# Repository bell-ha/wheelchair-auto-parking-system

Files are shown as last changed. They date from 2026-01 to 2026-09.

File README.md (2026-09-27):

<div align="center">

# 전동휠체어 자동 주차 시스템

운전하는 사용자를 위한 전동휠체어 적재






2025.12 ~ 진행 중 · 3인 팀 · 위치추정과 인식, 통합 담당 · ITRC 과제

</div>

---

## Impact

| | |
|---|---|
| **카메라를 옮긴 재설계** | 먼 구간이 안 찍혀 전면 개편 · 차량 어라운드뷰 → 휠체어 탑재 |
| **직접 구성한 데이터** | 실차 121장 · 목업 60장 직접 라벨링 · 차량 부품 6종, 번호판을 자로 활용 |
| **IMU로 회전 보정** | 앞바퀴가 캐스터라 틀어짐을 못 읽어, 각도 대신 회전속도를 맞춰 진동 제거 |
| **하드웨어 최적화** | 디코딩이 코어 하나를 91% 점유 · 갱신 주기 분리로 4 → 15 FPS 향상 |

---

## Background

전동휠체어 사용자는 차량에 탑승한 뒤, 밖에 남겨진 휠체어를 스스로 실을 수 없습니다.
이 과정에는 반드시 타인의 도움이 필요하고, 혼자 운전하는 사용자에게는 외출 자체의 제약이 됩니다.

본 연구에서는 **기아 RAY 자가운전 차량을 기준으로, 휠체어가 스스로 트렁크까지 가서
주차 및 출차하는 시스템**을 제안합니다.

설계 원칙은 처음부터 **범용성**이었습니다.

- 추가 센서 장착을 최소화한다
- 특정 차량·휠체어 모델에 종속되지 않는다
- 차량에 이미 달려 있는 것(어라운드뷰 카메라)을 최대한 활용한다

| | **V1** (중단) | **V2** (진행 중) | **V3** (검토) |
|---|---|---|---|
| 카메라 위치 | **차량** — 어라운드뷰 2대 | **휠체어** — 탑재 카메라 | 없음 |
| 무엇을 보나 | 휠체어의 ArUco 마커 | 차량 부위 6종 (딥러닝) | 전파 (UWB) |
| 위치 추정 | 탑뷰 맵 좌표 | 번호판 실측 규격 기반 단안 | 거리 측정 ±10 cm |
| 제어 | A\* 경로계획 → CAN | IBVS + 초음파 + IMU → 조이스틱 | |
| **막힌 곳** | **먼 구간이 안 보인다** | **하드웨어가 불어났다** | |

---

## Architecture

### V1 — 차가 휠체어를 본다

<div align="center">

</div>

### V2 — 휠체어가 차를 본다

<div align="center">

</div>

---

## Contributions

근거와 수식, 측정 전문은 [설계 노트](docs/DESIGN.md)에 있습니다.

### V1 — 차량 카메라로 위치 추정

차량에 장착되어 있는 어라운드뷰 카메라로 휠체어의 ArUco 마커를 보고 위치를 추정합니다.
휠체어에 아무것도 달지 않아도 되는, 범용성 원칙에 가장 충실한 선택이었습니다.

- 어안 왜곡을 편 뒤 SolvePnP로 마커까지의 위치와 회전을 구함
- 오차가 거리와 각도에 따라 일정한 방향으로 치우쳐, 그 편향을 학습으로 상쇄하는 보정층을 설계
- 칼만 필터로 시계열을 안정화

**8단계 파이프라인 중 7단계가 실기체에서 동작했습니다.**
캘리브레이션 → 탑뷰 합성 → 위치추정 → A\* 경로계획 → CAN 제어까지 이어졌습니다.

<div align="center">
<a href="https://youtu.be/o30saxUv7JM">

</a>
<br><sub>어안 2뷰(좌·후방)로 마커를 추적하고 탑뷰 맵에 위치를 찍는다 · <a href="https://youtu.be/o30saxUv7JM">youtu.be/o30saxUv7JM</a></sub>
</div>

### V2 — 휠체어 카메라로 위치 추정

휠체어에 실은 카메라로 차량의 특징을 봅니다.
공개 데이터셋이 실차에서 듣지 않아 직접 촬영하고 라벨링해 학습시켰습니다.

- 번호판, 엠블럼, 손잡이, 주유구, 후미등, 사이드미러 **부위 6종을 개별 탐지**
- **번호판을 기준 자로** 삼아 거리를 추정 — 335 × 155 mm가 국가 표준으로 고정되어 있음
- 목업을 학습시킨 뒤 **검출이 6배 증가**

<div align="center">
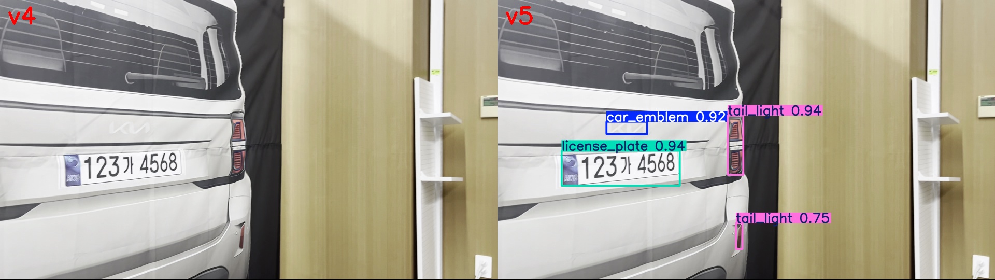
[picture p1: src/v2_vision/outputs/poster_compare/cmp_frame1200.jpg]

<br><sub>도메인 데이터 추가 학습 전(좌)과 후(우). 같은 프레임에서 검출 0건 → 4건</sub>
</div>

### 두 가지 센서로 정렬

사이드미러로 시야를 맞춘 뒤, 초음파로 평행을 맞춥니다.
한 센서로 끝까지 가지 않고 **구간마다 기준을 넘깁니다.**

- **VISION** — 사이드미러의 화면 위치와 크기를 목표 자세에 맞춤
- **SONAR** — 측면 초음파 앞뒤 거리 차이로 차량과 평행하게
- 두 국면 모두 **여덟 프레임 연속** 허용범위여야 다음으로 넘어감

<div align="center">

</div>

### 하드웨어 최적화

휠체어에 장착할 컴퓨터라는 제약에서 출발해 **Jetson Nano 4GB**에 얹었습니다.
4 FPS에 머물던 것을 지속 15 FPS, 프레임당 추론 42 ms로 끌어올렸습니다.

- 카메라를 30 fps로 받으면 디코딩 스레드가 **코어 하나를 91% 점유**해 추론이 쓸 CPU를 뺏음
- 카메라를 15 fps로 낮추고 화면 갱신을 10 Hz로 분리
- 모델 로드 중 프리징은 스왑 부족이어서 4 GB로 확장

| 처리 속도 | 프레임당 추론 | RAM | GPU | 전력 | 온도 |
|---|---|---|---|---|---|
| **지속 15 FPS** (최대 22) | 42 ms | 3.55 / 3.96 GB | 평균 35% | 5.8 W | 47~49 ℃ (팬 없음) |

---

## Troubleshooting

### 튜닝으로 풀 문제와 설계를 바꿔야 하는 문제

- **문제** 먼 구간의 오차가 줄지 않음. 보정을 더해도 그대로
- **원인** 거리가 멀어 그 구간이 아예 찍히지 않음. 파라미터로 풀 문제가 아니었음
- **해결** 마커를 키울 수도, 보정으로 메울 수도 없음. 그 근거로, 카메라를 휠체어로 옮기자고 제안
- **결과** V1에서 V2로 설계를 바꿈. 경로 생성은 그대로 쓸 수 있음. 팀원 작업은 영향 없음

> **캘리브레이션은 왜곡을 펴는 것이지, 찍히지 않은 곳을 보이게 하지 못합니다.**

<div align="center">

<br><sub>카메라를 고정된 쪽(차량)에 두느냐, 움직이는 쪽(휠체어)에 두느냐</sub>
</div>

### 직진 중 좌우로 진동

- **문제** 직진 명령을 줘도 똑바로 못 감. 좌우로 흔들림
- **원인** 앞바퀴가 캐스터라 이전 방향으로 휨. 그 틀어짐을 읽을 센서가 없음. IMU로 각도를 재 P제어로 되돌림. 방위오차가 1.2°인데 자이로는 −17.7°/s. 도착 순간 브레이크가 없어 반대로 넘어감
- **해결** 각도로 목표 회전속도를 정함. 자이로가 그 속도를 맞추는 구조로 교체. 적분항이 캐스터의 틀어짐을 주행 중 학습
- **결과** 가까울수록 스스로 감속. 50° 벗어난 상태에서 약 7초에 복귀

### Jetson Nano에서 프리징

- **문제** 추론을 돌리면 보드가 멈춤. 아무 응답이 없음
- **원인** 메모리가 모자라 스왑이 부족해짐
- **해결** 스왑을 4GB로 늘림. 입력 해상도를 320픽셀로 낮춤
- **결과** 15 FPS로 지속 구동. 추론에 42 ms

---

## 실행

Python 3.10 (`ultralytics`, `opencv-python`)

```bash
cd src/v2_vision

# 부위 탐지
python3.10 scripts/test_video.py raw_videos/레이영상_1.mov models/best_v5_poster.pt

# 거리·자세 HUD
python3.10 scripts/distance_video.py raw_videos/레이영상_1.mov models/best_v4_6cls.pt

# Jetson 실시간
cd jetson_nano && python3 main.py
```

결과 영상·데이터셋 원본 18개(약 3.8 GB)는 용량 제한으로 제외했습니다 (`.gitignore` 참고).

---

## 한계

### 자동으로 도는 구간 (1·2단계)

`AlignmentPlanner`가 VISION → SONAR 두 국면을 돌린다. 여기서 관측된 문제다.

| | 남은 문제 |
|---|---|
| 1. IBVS 초기 정렬 | 좌우로 진동하며 특징을 매칭하지 못하는 구간이 있다. YOLO를 올리며 메모리가 1 GB 늘어 **3.6 / 4 GB**까지 찼다 |
| 2. 초음파 평행 | 횡방향 간격은 잡히지만 **x축 정렬은 IBVS 오차가 크다** |

### 수동으로 이은 구간 (3~8단계)

**단계를 잇는 시퀀서를 붙이지 못했다.** 아래는 설계한 순서에서 예상되거나
수동 조작 중 관측한 것이지, 자동 주행에서 측정한 값이 아니다.

| 단계 | 남은 문제 |
|---|---|
| 3 · 5 · 8. 직·후진 | 캐스터 휠 정렬에 따라 이동 방향이 휜다. 직진 방위 유지만 IMU로 잡았다 |
| 4. 70° 회전 | **고정값이라** 시작 위치가 달라지면 따라가지 못한다 |
| 6. IBVS 후방 정렬 | 좌측 초음파 2개 간격이 짧고 완전한 후방이 아니라 매번 같은 위치로 수렴하지 않는다 |
| 7. IMU 정면 회전 | 전방 초음파가 하나뿐이라 평행 여부를 알 수 없어 IMU 오차가 그대로 남는다 |

### 장비와 기록

| | |
|---|---|
| **측면 초음파 4개가 전부 `-1`** | 전방은 정상. 2단계 SONAR 정렬이 지금 상태로는 돌지 않는다 |
| 텔레메트리 3 Hz | 초음파를 순서대로 재느라 느리다. IMU만 20 Hz로 따로 쏘면 보정 품질이 오른다 |
| `ultrasound/sample.ino` 불일치 | 실제 플래시된 펌웨어에 있는 MPU6050 코드가 저장소 버전에 없다 |

### V3 — 보지 않는 쪽으로

1·2·6은 시야에 의존하는 정렬이고, 3·5·8은 관측 불가능한 바퀴 상태에서 비롯된다.
개별 단계를 튜닝하는 대신 **시야에 의존하지 않는 측위**로 바꾸면 상당수가 함께 사라진다.
**UWB**를 검토 중이다 — 오차 ±10 cm, 현대·기아가 디지털키에 이미 상용화, 설치 위치·각도 제약이 적다.

> **조사와 장비 구매까지 진행했다. 실험은 시작하지 않았다.**

---

## 문서

| | |
|---|---|
| [설계 노트 (DESIGN)](docs/DESIGN.md) | V1 보정층 수식 · V2 학습 이력 · 9단계 설계 · V3 검토 |
| [V2 모델 학습 이력](src/v2_vision/README.md) | v1 → v5 학습 기록 |
| [거리추정 정리](src/v2_vision/거리추정_정리.md) | 핀홀 · yaw · bearing 유도 |
| [Jetson 부하 테스트](src/v2_vision/jetson_부하테스트_보고서.md) | 전체 측정 기록 |
| [세그멘테이션 실험](src/v2_vision/seg_experiment/RESULTS.md) | 대안 검토 |
| [V1 전체 정리](src/v1_aroundview/NOTES.md) | 8단계 파이프라인 |
| [발표자료](files/) | 0301 · 0821 · 0901 |
| [프로젝트 소개 페이지](https://bell-ha.github.io/projects/wheelchair-parking/) | 요약 · 도면 · 데모 |

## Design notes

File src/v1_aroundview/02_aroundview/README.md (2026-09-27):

# 02_aroundview — 탑뷰 합성

여기의 캘리브레이션은 어라운드뷰 전용이다. `01_calibration/` 의 것과 별개다.

| 파일 | 하는 일 |
|---|---|
| `calibration_left.py` · `calibration_rear.py` | 일반 카메라 캘리브레이션 |
| `aroundview_left.py` · `aroundview_rear.py` | 캘리브레이션 결과에 점을 찍어 어라운드뷰 생성 |
| `pickpoint.py` | `point_*.py` 가 쓸 점만 골라 저장 |
| `point_left.py` · `point_rear.py` | 저장한 점으로 어라운드뷰 생성 |
| `main.py` | Left·Rear 를 합쳐 하나의 캔버스로 |

`Data/` — 캘리브레이션 `.npz` 와 중간에 캡처한 데이터.

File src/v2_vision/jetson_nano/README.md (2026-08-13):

# jetson_nano — 젯슨 나노 배포용 폴더

카메라 실시간 추론 + 하드웨어(초음파/서보) 통합 코드 모음.
학습 코드·데이터셋은 없음 (추론 전용).

```
jetson_nano/
├── main.py                        # 통합 실행: 카메라(YOLO) + 초음파/서보(ESP32) 한 프로세스
├── hardware/                      # 🔧 공용 하드웨어 계층 — main.py와 guidance/가 같이 씀
│   ├── camera.py                  #   GStreamer 파이프라인 + Webcam (16:9/15fps 규칙 문서화)
│   └── esp32.py                   #   시리얼 프로토콜 한 벌 (텔레메트리 수신 + 서보 송신)
├── camera/
│   └── best_v5_poster.pt          # 최신 모델
├── ultrasound/
│   └── sample.ino                 # ESP32 펌웨어: 초음파 5개 + 서보 2축, JSON 프로토콜
├── guidance/
│   ├── teach.py                   # 목표 상태 저장 툴 (카메라+초음파 보면서 지도 클릭, s로 저장)
│   ├── guide.py                   # 판단: 정렬 지시 표시, --drive면 서보(조이스틱) 자동 구동
│   └── common.py                  # guidance 공용 (앵커 추출/좌표 추정/goal 저장·로드)
├── unused/                        # 대체된 코드 보관 (이유는 unused/README.md 참고)
├── requirements.txt
└── README.md
```

**구조 (3층):** 카메라/ESP32 접근 코드는 `hardware/` 공용 계층 한 벌뿐이고,
그 위에 사람조종용(`main.py`)과 판단용(`guidance/`)이 올라감 — 카메라 설정이나
시리얼 프로토콜이 바뀌면 `hardware/`(+펌웨어) 한 곳만 고치면 전체 반영됨.

## 젯슨 접속 (SSH)

맥과 젯슨이 같은 네트워크(같은 공유기)에 있어야 함. 계정 `jetson`, 호스트명 `nano`.

```bash
# 맥에서 — 호스트명으로 접속 (mDNS)
ssh jetson@nano.local

# 안 되면 IP로 (192.168.0.254)
ssh jetson@<JETSON_IP>
```

- IP 확인: 젯슨에서 `hostname -I`, 또는 공유기 관리 페이지 접속기기 목록.
- IP가 자꾸 바뀌면 공유기에서 DHCP 고정(예약) 해두기.
- 비밀번호 생략하려면 맥에서 한 번만: `ssh-copy-id jetson@nano.local`

## GitHub에서 받기

리포 전체는 수 GB라 이 폴더만 sparse checkout으로 받는다.

```bash
cd ~/GitHub
git clone --depth 1 --filter=blob:none --no-checkout \
    https://github.com/bell-ha/wheelchair-auto-parking-system.git
cd wheelchair-auto-parking-system
git sparse-checkout init --cone
git sparse-checkout set src/v2_vision/jetson_nano
git checkout main
cd src/v2_vision/jetson_nano
```

## Pull / Push

```bash
# 받기 (맥 등 다른 곳에서 push된 내용)
cd ~/GitHub/wheelchair-auto-parking-system
git pull

# 젯슨에서 수정한 거 올리기 (인증은 이미 설정돼있음)
git add -A
git commit -m "젯슨: 테스트 중 수정"
git push
```

작업 시작 전 `git pull`, 끝나면 바로 `push`. 같은 파일을 양쪽에서 동시에 고치면 충돌 남.

## 설치

```bash
pip3 install -r requirements.txt

# 주의: ultralytics가 opencv-python을 의존성으로 깔기 때문에 위 명령 직후
# GStreamer 미지원 pip opencv가 다시 설치돼있음. 반드시 지워서 JetPack
# 기본 OpenCV(dist-packages, GStreamer 지원)가 쓰이게 할 것 —
# 안 지우면 USB 웹캠(C920)에서 카메라 열기가 무한 대기함.
pip3 uninstall -y opencv-python
```

`ultrasound/sample.ino`는 아두이노 IDE로 ESP32 보드에 업로드 (젯슨 아님).
Jetson과 ESP32는 USB 케이블로 직결, 포트는 `/dev/ttyUSB0`, 115200bps.

## 실행 (통합 조종석 — main.py)

```bash
cd ~/GitHub/wheelchair-auto-parking-system/src/v2_vision/jetson_nano
python3 main.py        # 모델 경로 생략 시 camera/best_v5_poster.pt 사용
```

**키: A/D/W/S = 서보 수동 조작 | G = 자동모드 토글 | Q = 종료**

- **수동 모드(기본)**: A/D/W/S로 서보(조이스틱) 직접 조작
- **자동 모드(G)**: guidance 판단기가 teach로 저장한 goal을 향해 서보를 스스로
  조작. **자동 중 아무 이동키나 누르면 즉시 수동 복귀 + 정지** (비상 개입).
  goal 파일이 없으면 자동모드는 비활성 (화면에 사유 표시)
- **터미널(curses)**: 검출/FPS, 자동모드 지시·판단근거(du/scale/sonarErr)·전송각,
  초음파 5개, 서보 에코, 수신시간을 실시간 표시
- **HDMI 카메라 창**: 검출 박스 + 목표 ✕마커 + 현재 앵커 ○ + 자동모드 지시 배너 +
  오른쪽에 미니맵(CAR·목표·현재위치 추정). 기본 절반 크기(`--display-scale 0.5`),
  `--no-show`로 끄기 가능
- ESP32가 안 붙어있으면 `--no-servo`로 카메라만 테스트. 그 외 `--help`
- 자동모드 서보 방향이 반대면 `--invert-x`/`--invert-y`, 편향각은
  `--turn-deg`/`--drive-deg` (기본 ±10°)

시작 직후 "모델 워밍업 중..."이 30초~1분 정도 뜨는 건 정상 (젯슨 첫 추론 특성).
워밍업이 끝나야 터미널 화면으로 전환됨.

`--cam-width`/`--cam-height`는 16:9 조합(1280x720, 1920x1080 등)으로 맞출 것 — C920은
4:3 해상도(640x480, 800x600, 1280x960)를 요청하면 카메라 자체가 좌우를 크롭해서
화각이 좁아짐. 1920x1080은 화면은 더 선명하지만 이 보드(RAM 4GB) 기준 메모리 여유가
빠듯해서(스왑 발생 확인됨) 1280x720 권장.

부품 단독 점검: 카메라만 → `main.py --no-servo`, ESP32만(카메라 없이) →
`unused/test_sample.py` 꺼내 쓰기 (자세한 건 unused/README.md).
부하 확인은 다른 터미널에서 `sudo tegrastats` 병행 권장 (GPU 사용률·온도·스로틀링).
자세한 결과는 [../jetson_부하테스트_보고서.md](../jetson_부하테스트_보고서.md) 참고.

## 자동 정렬 (guidance/)

teach & repeat 방식: `teach.py`로 목표 상태(사이드미러 위치·크기 + 측면 초음파 쌍 +
지도에 클릭한 목표 좌표)를 JSON으로 저장해두면, 판단기(`common.AlignmentPlanner`)가
현재 상태와 비교해 "TURN LEFT / MOVE FORWARD / ALIGNED - STOP" 지시를 만듦.
①VISION 단계(사이드미러 정렬) → ②SONAR 단계(측면 초음파 앞/뒤 차이로 평행 정렬) 순서.

**판단기는 main.py 자동모드(G키)와 guide.py가 공유** — 평소엔 main.py G키가
주 사용 경로고, guide.py는 guidance만 따로 돌리고 싶을 때의 단독 진입점.

```bash
python3 guidance/teach.py            # (선행 필수) 목표 저장: 지도 클릭 + s, q 종료
python3 guidance/guide.py            # 단독 실행: 지시 화면 표시만 (기본, 안전)
python3 guidance/guide.py --drive    # 단독 실행 + 서보(조이스틱) 실제 구동
```

`--drive` 모드: TURN/MOVE 지시가 서보 X/Y 편향(기본 ±10°, `--turn-deg`/`--drive-deg`)으로
전송되고, STOP류 지시·타겟 상실·종료 시엔 무조건 중앙(90/90=정지)으로 복귀함.
**첫 구동 테스트는 반드시 휠체어 전원을 끄거나 바퀴를 띄운 상태에서** 서보가
의도한 방향으로 움직이는지 확인하고, 반대로 움직이면 `--invert-x`/`--invert-y`로 보정.

- 카메라·시리얼을 main.py와 공유하므로 **동시 실행 불가**
- 초음파 기준 거리(SONAR_BASELINE=0.315m)는 `sample.ino`의 `SIDE_SENSOR_SPACING_CM=31.5`와
  맞춰둔 값 — 센서 간격을 바꾸면 양쪽 다 수정할 것

## 젯슨나노 종료
```bash
sudo shutdown -h now
```

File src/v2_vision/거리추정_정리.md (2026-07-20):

# 거리·각도 추정 작업 정리 (2026-07-09~10)

휠체어프로젝트의 다음 단계 작업 기록. README.md(프로젝트 전반)와 함께 읽을 것.

## 무엇을 만들었나

`scripts/distance_video.py` (신규) — v4 탐지 모델 위에 **번호판 실측 규격 기반
단안 거리·각도·방위각 추정**을 얹은 스크립트. 기존 test_video.py는 안 건드림.

실행:
```
python3.10 scripts/distance_video.py raw_videos/레이영상_1.mov models/best_v4_6cls.pt --conf 0.15
```
결과는 `outputs/distance/<영상>_dist.mp4` (좌상단 HUD로 값 표시).
※ 환경 주의: ultralytics/opencv는 **python3.10**(Frameworks)에 설치돼 있음.
README에는 3.11로 적혀 있는데 실제로는 3.10 (README 미수정).

## HUD에 표시되는 3가지 값 (도킹 제어의 3요소)

| 값 | 계산 방법 | 의미 (휠체어 관점) |
|---|---|---|
| 거리 (m) | 번호판 높이 155mm × 핀홀 공식: D = H_real·f / h_px | 얼마나 남았나 |
| yaw (deg, ±) | 크기 = 폭/높이 비율 acos, 부호 = 꼭짓점 키스톤(좌/우 변 길이 비교). 음수 = 왼쪽(L)에서 봄 | 차가 얼마나 비스듬한가 → 접근 자세 |
| bearing (deg, ±) | atan((번호판 중심 x − 화면중심) / f). 왼쪽 음수 | 차가 내 시야 어느 쪽인가 → 조향 |

- 레이 후면 번호판 실측 규격: **단형 335×155mm** (영상에서 육안 확인, "66라 5623")
- 초점거리: iPhone 13 mini 1x(35mm환산 26mm) 가정 → 1920px 기준 f≈1387px.
  **미보정 상태라 거리에 ±10~15% 스케일 오차 가능.** 줄자로 잰 거리에서 찍은
  영상으로 `--calib 1.0` 실행하면 `scripts/camera_calib.json`에 저장돼 자동 보정됨 (아직 안 함)
- 모든 값은 EMA(α=0.3)로 프레임 간 스무딩

## 핵심 구현 디테일 (수정 시 알아야 할 것)

1. **화면 경계에 잘린 번호판은 무시** — 잘린 박스는 작게 잡혀 거리가 부풀려짐
2. **yaw 부호(키스톤)**: YOLO 박스 크롭 → Otsu 이진화 → `RETR_LIST`(내부 윤곽 포함;
   흰 차체가 번호판을 둘러싸면 번호판 면이 blob 속 구멍이 되기 때문) → 4각형 후보 중
   크롭 경계에 안 닿는 것 우선 → 크기(YOLO 박스의 0.5~1.2배)·비율(0.6~4.5) 검증.
   좌/우 변 길이는 유클리드 거리(카메라 roll에 안전). 검출 실패 시 부호 없이 "(?)"
3. **키스톤으로 각도 "크기"까지 재는 건 포기** — 꼭짓점 1~2px 오차에 수십 도가
   흔들림(실측 -46° 오류 경험). 크기는 비율(acos) 방식이 안정적
4. `iou=0.5`로 predict — 같은 부위 중복 박스 억제
5. "가장 큰 번호판 박스"를 추적하므로 **다른 차 번호판을 따라갈 수 있음** (목표 차량
   필터 미구현 — 알려진 한계)

## 후미등 간격 방식 (실험, `--tail` 플래그, 기본 꺼짐)

아이디어: 번호판이 좌우 후미등의 정중앙(간격 실측 추정 1.3m) → 좌우 간격 비대칭으로
부호 있는 yaw. 기준선이 길어 원거리에서 유리할 것으로 기대했으나 실영상 검증 결과:
- 근거리(<3m): 후미등이 모서리를 감싸는 입체 렌즈라 박스 중심이 밀려 각도 과장
- 원거리(>7m): 신호가 거리²에 반비례해 박스 떨림에 묻힘 (±90° 포화)
- 다중 차량: 다른 차 후미등과 짝지어짐
방어 장치(위/아래 쌍 매칭 + 두 쌍 일치 검증 + 물리 크기 검증 + 3~7m 게이트)를 넣어
자기모순은 없어졌지만, **현재 영상 3개에는 레이가 3~7m 후면에 나오는 구간이 없어서
레이 대상 검증 미완**. 살리려면 7~8m 후면 직진 접근 영상 필요.

## 검증된 결과 (실영상 육안 확인)

- 정면 1.2m 후면: 거리 1.20m, yaw ~0(front) ✓
- 후면 오른쪽 45° (영상1 1초): 1.48m, **yaw +49°(R)**, bearing -21° ✓ (부호 모두 정확)
- 좁은 통로 오른쪽 비스듬 (영상3 20초): 0.83m, **+66°(R)** ✓
- 왼쪽 치우친 후면 (영상1 10초): -25°(L) ✓
- 거리 중앙값: 영상1 1.48m / 영상2 4.11m / 영상3 0.87m (장면과 부합)

## 센서/하드웨어 계획 (사용자 구상)

- **카메라를 팬 모터에 장착 예정** → 모터가 번호판을 화면 중앙에 추적.
  이때 화면상 bearing은 모터 제어 오차 신호가 되고, **모터 인코더 각도가 곧
  "휠체어 몸통 기준 차의 방향"**(= 조향 신호). yaw는 카메라를 돌려도 안 변함
  (위치 관계로 정해지는 값). 통합 시 `총 bearing = 모터각 + 화면 bearing`
- **초음파 센서**: 최근접(<1m) depth + 충돌 방지 담당. 비전은 식별·정렬 담당

## 다음 할 일

1. 촬영 1세션으로 3가지 해결: (a) 캘리브레이션용 줄자 1.0m 컷,
   (b) 후미등 방식 검증용 7~8m 후면 직진 접근, (c) 실배치 특화용 다각도 촬영
2. **v5 학습 계획**: `sliding_door`(+ 필요시 `door_open`) 클래스 추가 — 레이는
   조수석 쪽이 B필러 없는 슬라이딩 도어(휠체어 승하차 방향). 공공 데이터에 없으니
   후미등 때처럼 레이 데이터 + 오버샘플링. 미러 데이터도 보강(오탐 확인됨, mAP .754)
3. 문손잡이: 거리 측정용으론 부적합(3D 곡면, 박스 비율 0.14~5.6 요동 실측).
   **조향 목표(bearing) + 차 기하 결합**으로 사용. 앞문/슬라이딩문 손잡이 구분 필요
4. 목표 차량 필터(다른 차 번호판 배제 — 엠블럼·후미등 동반 검출 활용)
5. `git init` (잘 짜인 .gitignore가 이미 있는데 저장소가 아님)
6. README 환경 표기 수정 (python3.11 → 3.10)

## 파일 목록

- `scripts/distance_video.py` — 본 작업의 산출물 (docstring에 사용법·원리 상세)
- `outputs/distance/*_dist.mp4` — 기본 결과 3개 (영상1만 bearing 포함 최신,
  영상2·3은 bearing 추가 이전 버전)
- `outputs/distance/*_dist_tail.mp4` — `--tail` 실험본.
  ※ 영상2 tail본은 tail 미발동으로 기본본과 완전 동일(340MB 중복, 삭제 가능)
- `scripts/camera_calib.json` — 아직 없음 (캘리브레이션 후 생성됨)

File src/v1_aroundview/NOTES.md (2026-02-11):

# 프로젝트 요약 정리 (Localization / Around-View 기반 휠체어 트래킹)

## 0) 목적 및 개요

* 차량 어라운드뷰(서라운드뷰) 카메라 2대(Left, Rear)로 휠체어에 부착된 ArUco 마커를 감지하여 휠체어의 위치를 추정한다.
* 제어 신호는 4가지:

  * **F**(전진), **B**(후진), **R**(오른쪽 회전), **L**(왼쪽 회전)

---

## 1) 카메라 캘리브레이션 데이터 (Localization 용)

### 1-1. 공통 데이터

두 카메라가 동일 렌즈 모델이라 파라미터를 공유한다.

* **Camera Matrix (`K`)**

  * `[[601.719, 0, 630.477], [0, 601.345, 367.212], [0, 0, 1]]`
  * 의미: 초점거리 및 주점(중심점)

* **Distortion (`D`)**
  * `[-0.18496, 0.02541, -0.01068, 0.00322]`
  * 의미: Fisheye 왜곡 계수
  
* **Marker Size (`size`)**
  * 0.25 m (25 cm) : ArUco 마커 실제 크기

* **RMS Error (`rms`)**
  * **0.5898**
  * 메모: “시스템 신뢰도(양호)”로 판단

### 1-2. 카메라별 설치/제어 보정값 (Extrinsic & Control)
설치 위치가 다르므로 각도 계산/제어용 보정값을 카메라별로 적용한다.

| 항목            | Rear(후방) | Left(측방) | 설명                          |
| ------------- | -------: | -------: | --------------------------- |
| 각도 감도 `SENS`  |      1.6 |      1.6 | 어안 외곽 압축 상쇄 + 실제 각도 동기화     |
| 설치 보정각 `INST` |      0.0 |    113.0 | Left: 서쪽 90° + 남쪽 23° 편향 상쇄 |
| 영점 오프셋 `OFFS` |      0.0 |    50.84 | 휠체어 정북향 시 최종 Yaw를 0으로 고정    |

---

## 2) 차량/레이(차체) 기본 치수 가정

* **폭(차량 + 사이드미러 포함)**

  * 1595mm + 사이드미러 각 178mm = **1951mm ≈ 약 2m로 가정**

* **길이(전장)**
  * 3595mm = **약 3.6m로 가정**

참고 링크(자료 출처로 사용 예정):

* [https://carmia.co.kr/html/s0603.php?d=v&tbl=b0603&seq=833&page=1&s_sel=&s_key=&s_cat=](https://carmia.co.kr/html/s0603.php?d=v&tbl=b0603&seq=833&page=1&s_sel=&s_key=&s_cat=)
* [https://m.oh-car.co.kr/goods/goods_view.php?goodsNo=1000593989](https://m.oh-car.co.kr/goods/goods_view.php?goodsNo=1000593989)

---

## 3) 어라운드뷰 카메라 설치 위치/각도 (추정 포함)

### 3-1. Left 카메라 (사이드미러 아래)

* **설치 위치**: 차량 왼쪽, 사이드미러 아래
* **설치 높이**: 1100mm

* **Pitch(아래 바라보는 각도)**
  * 실제 설정: **40도**(아래에서 20도라고 했으나, 40도까지밖에 안됨)

* **Yaw(좌우 방향)**
  * 정확한 수치는 없음
  * “앞 뒤 다 나오게” 조정
  * 추가로: 왼쪽 자체를 바라보는 방향에서 더 뒤로 23도 틀어져 있음 -> 157도

### 3-2. Rear 카메라 (번호등 아래)

* **설치 위치**: 차량 후면 중앙 번호등 아래
* **설치 높이**: 1055mm

* **Pitch(아래 바라보는 각도)**
  * SVM 매뉴얼 기준: 아래로 5~60도(범위 언급)
  * 실제 사용: 
  50도

---
## 4) 휠체어(실제) 정보 + 마커 정보

### 4-1. “실제 휠체어(기본)” 치수 및 마커(초기 설명)
* **휠체어 폭/길이**
    * 폭 57cm, 길이 100cm

* **앞 ID:0**
  * 마커 높이:70c
  * 13도 위를 향함

* **뒤 ID:1**
  * 마커 높이: **56cm**
---

## 5) “휠체어 없이 트래서(Tracker) 운용” 시나리오(별도 세팅)
* 앞 ID:0 마커 높이: 70cm
* 뒤 ID:1 마커 높이: 70cm
* 대상 폭/길이
  * 폭 55cm, 길이 66cm

---

## 6) 지도/프레임 좌표계 및 금지구역(차량 영역)

* 전체 프레임: **1500 x 1500**
* 어라운드뷰 프레임: **600 x 720**(1500x1500기준에서 중앙)
* 어라운드뷰 프레임 내 **자동차 구역(진입 불가 폴리곤/사각형)**
  * 꼭짓점: **(200,180), (400,180), (400,540), (200,540)**(어라운드뷰 프레임 기준)
  * 이 영역 안으로는 들어갈 수 없음(경로 계획/제어에서 회피해야 함)

---

## 7) 카메라 기준 좌표(설치 위치) 및 목표 위치(주차/출차)(어라운드뷰 프레임 기준)

* 카메라 위치
  * **Left 카메라 위치: (200, 270)**
  * **Rear 카메라 위치: (300, 540)**

* 주차 시(도킹/정렬) 목표 상태:
  * **(300,600)** 위치에서 **Rear를 바라보고 있는 상태**

* 출차 시 목표 상태:
  * **(150,360)** 위치에서 **Left를 바라보고 있는 상태**

---

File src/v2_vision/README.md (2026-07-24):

# 휠체어프로젝트 — 자동차 부위 탐지 (YOLOv8)

전동휠체어가 차량에 접근/인식하기 위한 자동차 부위 6종 탐지 모델.

## 전역 클래스 표준 (자연어 언더바, nc=6)
0:car_emblem  1:door_handle  2:fuel_cap  3:license_plate  4:side_mirror  5:tail_light

## 폴더 구조 (2026-07-23 정리)
- raw_datasets/ : 원본 Roboflow zip (건드리지 않음). 공공 6종 + ray_roboflow_v1.zip
- models/ : best_v1_merged / best_v2_ft / best_v3_ray / best_v4_6cls(최신)
- raw_videos/ : 원본 영상 — 레이영상 1·2·3(실차) + 포스터레이.MOV(실물크기 포스터, 포스터 라벨의 원본)
- my_data/labeled/ray_all/ : 실차 라벨 데이터 (6종, 121장) ★
- my_data/labeled/ray_poster/ : 포스터 라벨 데이터 (6종, 60장, 2026-07 추가) ★
- scripts/ : test_video.py, distance_video.py, live_camera.py, finetune_local.py,
             kaggle_finetune_v3.ipynb, kaggle_finetune_v4.ipynb (remap_ray.sh는 5클래스 시절 유물 — 사용 금지)
- outputs/ : 결과 영상 (v4 검출 3개 + distance HUD 3개만 보존. v3·tail 실험본은 삭제 — 스크립트로 재생성 가능)
- seg_experiment/ : 세그멘테이션 실험 기록 (RESULTS.md + 스크립트만 보존, 대용량 삭제)
- kaggle_upload/ : Kaggle 업로드용 공공 6종 .bin 로컬 백업 (캐글 데이터셋 유실 대비.
  raw_datasets zip과 내용 동일, 이름만 노트북 SOURCES 기준)
- my_data/labeled/ray_all.bin·ray_poster.bin : 라벨 폴더에서 재생성되는 업로드용 압축본 (git 미추적)

## 모델 버전 이력
- v1_merged : 5종 개별→통합. 번호판 배경충돌로 억제됨
- v2_ft     : 신형 번호판 fine-tune. 레이영상 plate 13→80프레임
- v3_ray    : 레이 도메인 데이터(5종) 추가 fine-tune. 번호판 실영상 개선
- v4_6cls   : 후미등(tail_light) 추가, 6클래스 새 학습 (2026.07.06)
              val mAP50: plate .995 / emblem .974 / handle .917 /
              fuel_cap .878 / tail_light .811 / mirror .754
- v5_poster : 포스터(실물크기 목업) 60장 추가, POSTER_REPEAT=12 독립 소스 (2026.07.24) ★최신
              포스터 환경 대폭 개선 (plate 검출 프레임 6배, conf 0.26→0.89)
              ※ 실차 성능 재검증 미완 — 자세한 내용은 포스터_위치추정_정리.md

## 학습 방법 (요약)
- Kaggle T4에서 학습. 노트북: scripts/kaggle_finetune_v4.ipynb
- Add Input: 공공 6종 bin + ray_all.bin (한 데이터셋에 다 넣어도 됨)
- 자세한 준비/업로드 순서: kaggle_학습방법.md 참고
- 클래스 5→6 바뀌어 v3 이어받기 불가 → yolov8n부터 새 학습
- 레이는 후미등 유일 출처라 oversampling(RAY_REPEAT)으로 비중 확보

## 다음 할 일 (2026-07-24 갱신 — 상세는 포스터_위치추정_정리.md '남은 일')
- 포스터 줄자 실측 4개 → 위치추정 랜드마크 좌표 확정
- f 캘리브레이션 (--calib), v5 실차 성능 확인 (레이영상 1~3 재실행)
- 도킹 제어 개발 (진입점 계산 → 2단계 접근 → IBVS 정밀 정렬)

## 핵심 교훈
1. 부분 라벨=배경충돌: 병합 시 라벨 안 된 대상이 배경으로 학습돼 검출이 죽음
   (번호판 v1, 후미등도 공공데이터엔 없어 레이로만 배움)
2. 리허설 fine-tune: 새 데이터+기존 클래스 일부를 섞으면 망각 없이 특정 클래스 보강
3. val≠실전: val 지표 높아도 진짜 판정은 "내 영상에서 몇 프레임 잡히나"
4. 도메인 불일치가 진짜 원인: 해결은 학습량이 아니라 내 영상 도메인 데이터
5. 클래스 추가 시 재매핑: Roboflow 알파벳순 → 전역 표준 순서로 맞춰야 함
   (auto-label은 세그멘테이션 라벨 뱉음 → 박스 변환 필요. v4 노트북이 자동 처리)

## 환경 메모
- 로컬 맥: python3(3.14)는 MPS 안 됨. python3.11 사용 (opencv 등은 3.11에 설치)
- 추론: python3.11 scripts/test_video.py <영상> <모델.pt> <conf>
- 학습은 Kaggle T4 권장 (무료, 환경문제 없음)
- Kaggle zip data.yaml 충돌 → .bin으로 확장자 바꿔 회피

## 다음 단계: 실배치 레이 특화 (계획)
- 실제 테스트/배치할 레이 1대를 확정
- 그 차를 다양한 상황(각도·거리·조명·낮밤)으로 충분히 촬영·라벨링
- 일반화보다 "그 차 확실히 잡기" 목표 → 해당 레이에 의도적으로 특화(overfit 허용)
- 주의: "한 대"여도 다양한 상황이 필요 (같은 장면만 과적합하면 실주행서 약함)
- RAY_REPEAT 높이고, 그 차 데이터 비중 크게 잡아 학습

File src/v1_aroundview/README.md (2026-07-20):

# V1 — 차량 어라운드뷰 기반 (개발 중단)

차량에 장착한 어라운드뷰 카메라 2대(Left, Rear)로 휠체어에 부착된 ArUco 마커를
검출해 휠체어 위치를 추정하고, A* 경로계획으로 제어 신호(F/B/L/R)를 만들어
휠체어를 차량 옆 주차 위치까지 유도하는 파이프라인.

> **중단 사유**: 어안(fisheye) 카메라 캘리브레이션의 누적 오차로 맵 좌표가 튀는
> 문제를 07_map_calibration에서 끝까지 잡지 못함. 카메라를 차량이 아닌
> **휠체어에 탑재**하는 방식([V2](../v2_vision/))으로 전환.

## 환경 설정

```bash
source ../venv/bin/activate   # 가상환경 (repo에는 미포함)
pip install -r requirements.txt
```

## 폴더 구성 (파이프라인 순서)

| 폴더 | 내용 |
|---|---|
| `01_calibration/` | 체커보드 촬영 → 카메라 왜곡계수 추출 |
| `02_aroundview/` | Left/Rear 영상 정합 → 어라운드뷰(탑뷰) 합성 |
| `03_localization/` | ArUco 마커 검출로 휠체어 위치/방향 추정, 맵 생성 |
| `04_planning/` | A* 기반 경로계획 |
| `05_hardware/` | 구동부: TRACER 섀시 CAN 통신 제어 절차 |
| `06_angle_tunning/` | 각도 보정(트랙바 UI로 파라미터 튜닝) |
| `07_map_calibration/` | 최종 맵 캘리브레이션 — 오차 가중 보정, outlier 제거 시도 |
| `08_parking/` | 통합 실행: 위치추정 + 경로계획 + 제어 (수동조종 포함) |
| `command/` | 03/06 계열 통합 실험 버전 |
| `utils/` | 카메라 탐색, 녹화, ArUco 검출 등 보조 도구 |

## 기술 노트

캘리브레이션 수치, 카메라 설치 위치/각도, 좌표계 정의 등 상세 기록은
[NOTES.md](NOTES.md) 참고.

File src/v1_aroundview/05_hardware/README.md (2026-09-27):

# 05_hardware — 구동부와 차량 사양

TRACER 섀시 CAN 통신 절차는 [can_bus/README.md](can_bus/README.md) 에 있다.

## 기아 레이 내비게이션 사양 (조사)

| | |
|---|---|
| 화면 | 8인치 터치스크린 |
| CPU | 차량용 프로세서 — Nvidia Tegra 또는 Telechips 계열로 **추정** |
| RAM | 2~4 GB **추정** |
| 연결 | 기아 커넥트 — 내장 eSIM, OTA 업데이트 |

> **추정 근거** — 현대차 하드웨어가 5세대에서 RAM 2~4 GB 였고 이후 4~8 GB 로 올라갔다.
> 주요 공급사 텔레칩스의 Dolphin 시리즈 가이드에도 메모리 구성이 2~4 GB 로 나온다.
> **제조사 공식 사양이 아니다.**

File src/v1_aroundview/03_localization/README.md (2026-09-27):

# 03_localization — 휠체어 검출

| 파일 | 하는 일 |
|---|---|
| `angle_focus.py` | Left·Rear 영상에서 휠체어 검출 |
| `angle_focus_live.py` | 실시간 영상에서 휠체어 검출 |
| `main.py` | Left·Rear 에서 검출하는 최종본 |

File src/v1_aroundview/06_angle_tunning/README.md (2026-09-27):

# 06_angle_tunning — 각도 보정

트랙바 UI 로 파라미터를 맞춘다.

| 파일 | 하는 일 |
|---|---|
| `main.py` | 통합 실행 · 트랙바와 시각화 UI |
| `localization.py` | ArUco 기반 휠체어 위치·방향 추정 |
| `planner.py` | A* 경로 계획 |
| `tracker.py` | 경로 추종과 재계획 관리 |
| `visualizer.py` | 맵·경로·휠체어 상태 시각화 |

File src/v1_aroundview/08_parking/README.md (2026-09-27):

# 08_parking — 통합 실행

위치추정 · 경로계획 · 제어를 한데 묶어 돌린다.

| 파일 | 하는 일 |
|---|---|
| `main.py` | 통합 실행 |
| `control.py` | `wasd` 로 수동 조종, `x` 로 정지 |
| `localization.py` | 위치 추정 |
| `phase.py` | 단계 관리 |

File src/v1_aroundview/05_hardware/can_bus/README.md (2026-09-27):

# CAN 통신 — AgileX TRACER 섀시 제어

USB-CAN 으로 TRACER 섀시에 명령을 넣는 절차. A → F 순서로 따라간다.
**리모컨 권한을 반납(E)해야 CAN 명령이 먹고, 전진은 주기 전송이어야 한다(F).**

## A. PC(리눅스) 준비 체크리스트

### A-1) USB-CAN 인식 확인

```bash
lsusb
```

*  `OpenMoko ... CAN adapter`면 보통 `gs_usb` 계열이라 SocketCAN 바로 가능.

### A-2) 필수 패키지

```bash
sudo apt update
sudo apt install -y can-utils
```

```bash
pip3 install python-can
```

### A-3) 드라이버 로드(필요시)

```bash
sudo modprobe gs_usb
```

### A-4) can 인터페이스 생겼는지 확인

```bash
ip link | grep -E "can[0-9]"
```

* `can0` 또는 `can1`이 보여야 정상

---

## B. TRACER ↔ USB-CAN 배선 표준

1. 로봇 전원 **OFF 권장** 상태에서 배선

* **CAN_H ↔ CAN_H**
* **CAN_L ↔ CAN_L**

2. 로봇 전원 ON
* **E-stop 해제**
* 주변 안전 확보

---

## C. CAN 통신 “켜기” (비트레이트 포함)

TRACER는 **500kbps**.

```bash
sudo ip link set can0 up type can bitrate 500000
```

(인터페이스가 can1이면 can1로)

---

## D. “로봇이 말하는지(피드백)” 먼저 확인

이게 되면 배선/비트레이트/물리계층은 통과야.

```bash
candump can0
```

너처럼 `0x211`, `0x221`, `0x231` 등이 주기적으로 보이면 정상.

---

## E. 핵심: 리모컨 권한 반납(= CAN 제어 모드로 전환)

### E-1) 현재 모드 확인 (0x211)

```bash
candump can0,211:7FF
```

출력 예시:

* `00 00 ...` → **RC 모드**
* `00 01 ...` → **CAN 모드**
* `00 02 ...` → **Serial 모드**

### E-2) CAN 모드로 전환 명령 (ID 0x421)

RC를 꺼둬도 내부 모드가 RC로 남아있을 수 있어서, 이걸로 CAN 통신 전환

```bash
cansend can0 421#01
```

다시 확인:

```bash
candump can0,211:7FF
```

`00 01 ...`로 바뀌면 **모드 전환 성공**.

> 이 단계가 바로 네가 말한 “리모컨 권한 반납”에 해당.

---

## F. 전진 테스트(주기 전송이 필수)

TRACER는 보호 때문에 **500ms 이상 명령이 끊기면 0속도**로 떨어져.
그래서 “한 번 보내기”가 아니라 **20ms 주기 전송**이 필요.

아주 느리게 전진(100mm/s):

```bash
while true; do cansend can0 111#0064000000000000; usleep 20000; done
```

멈춤: `Ctrl+C`

속도 피드백 확인(선택):

```bash
candump can0,221:7FF
```

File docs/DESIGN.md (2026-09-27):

# 설계 노트

V1 에서 V2 로 넘어오며 무엇을 보고 왜 그렇게 정했는지를 남긴 글이다.
무엇을 만들었는지는 [README](../README.md) 에 있다.

수식·측정값·파일 줄 번호는 전부 당시 코드와 실험 기록에서 직접 확인한 것이다.

---

## 3. V1 — 차가 휠체어를 본다

차량에 이미 달린 어라운드뷰를 쓰면 **휠체어에 아무것도 달지 않아도 된다.** 원칙에 가장 충실한 선택이었다.

어안 카메라 2대를 캘리브레이션해 탑뷰를 합성하고, 휠체어에 붙인 25×25 cm ArUco 마커로 위치를 추정했다.

| 좌측 카메라 | 후방 카메라 | 합성 결과 |
|---|---|---|
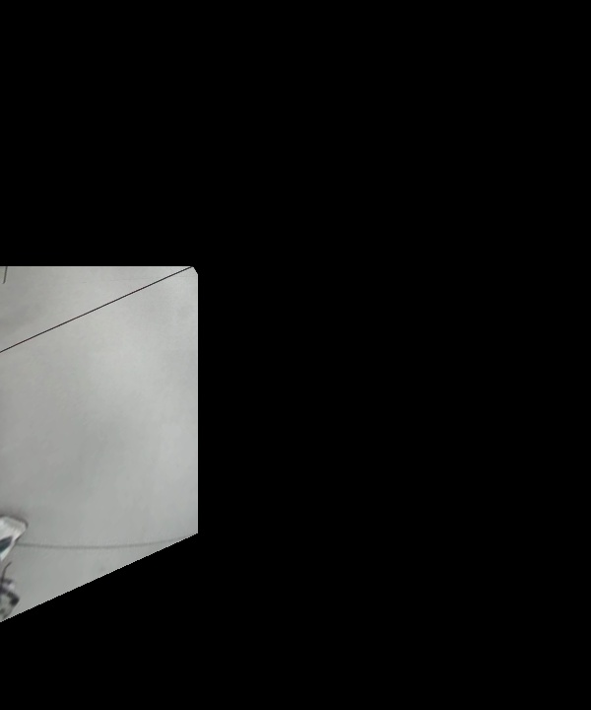
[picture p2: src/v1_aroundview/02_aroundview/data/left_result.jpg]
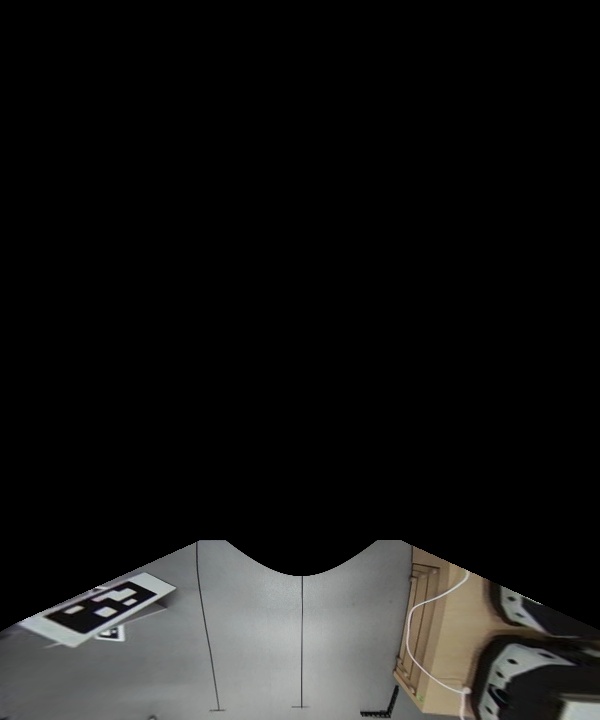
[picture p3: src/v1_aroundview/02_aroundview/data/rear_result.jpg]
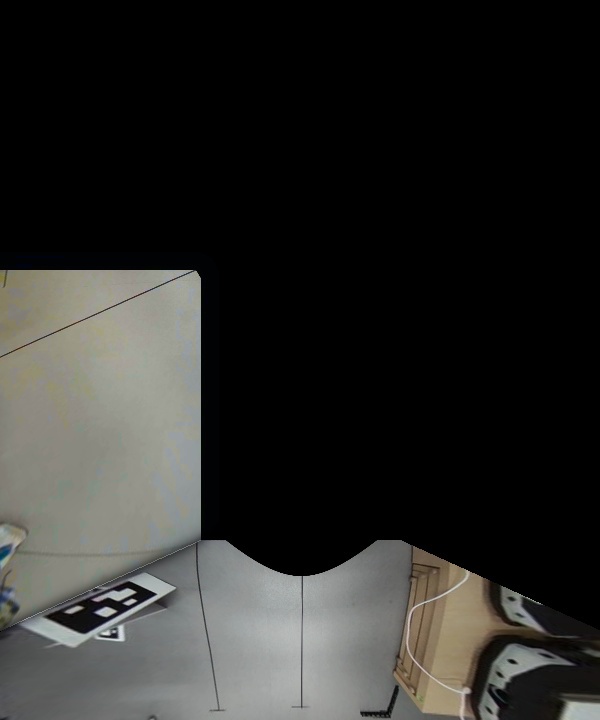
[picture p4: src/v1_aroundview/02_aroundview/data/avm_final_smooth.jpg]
|  |  |  |

### 잔차가 무작위가 아니었다

SolvePnP 결과를 그대로 쓰지 않았다. **출력 잔차가 거리·각도에 따라 체계적으로 편향된다**는 것을 확인하고 보정층을 학습으로 설계했다.

```
X = [1, g, g², b, b², v, g·b, reproj]     g 바닥거리(m) · b 화면 내 마커 각도(deg)
w* = argmin ‖Xw − y‖² + λ‖w‖²             v 마커가 카메라를 보는 각도 · reproj 재투영 오차(px)
```

여기에 전·후진 200 mm/s · 회전 0.3 rad/s 운동 모델의 칼만 필터를 얹어 시계열을 안정화했다.

| 맵 보정 전 | 보정 후 |
|---|---|
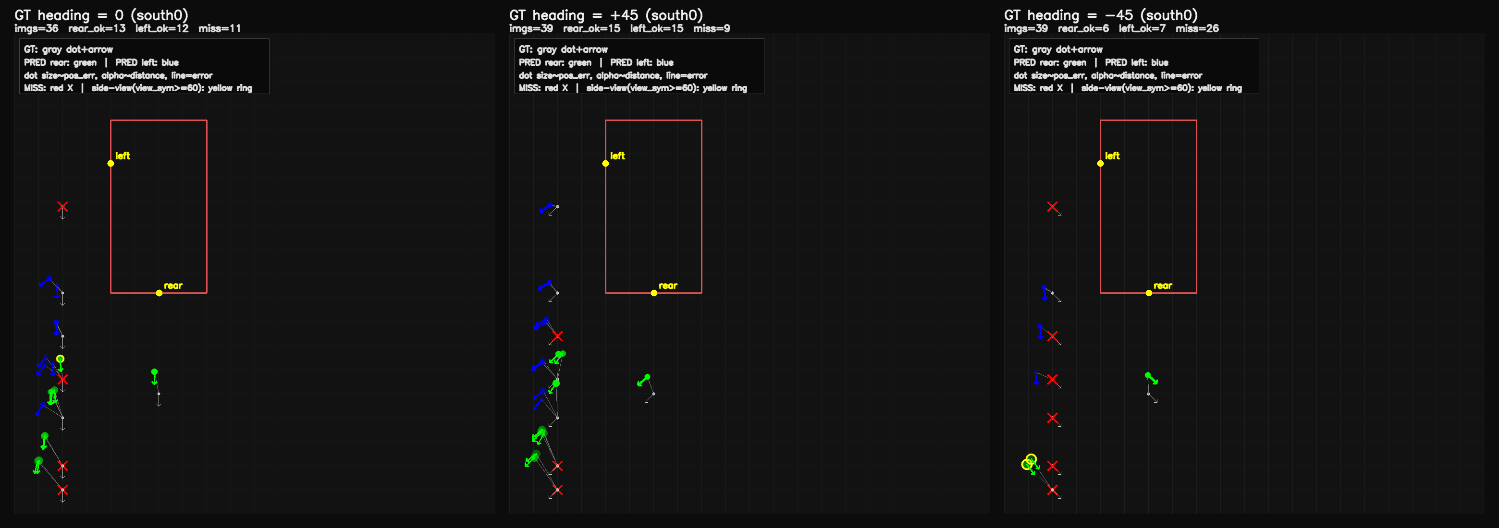
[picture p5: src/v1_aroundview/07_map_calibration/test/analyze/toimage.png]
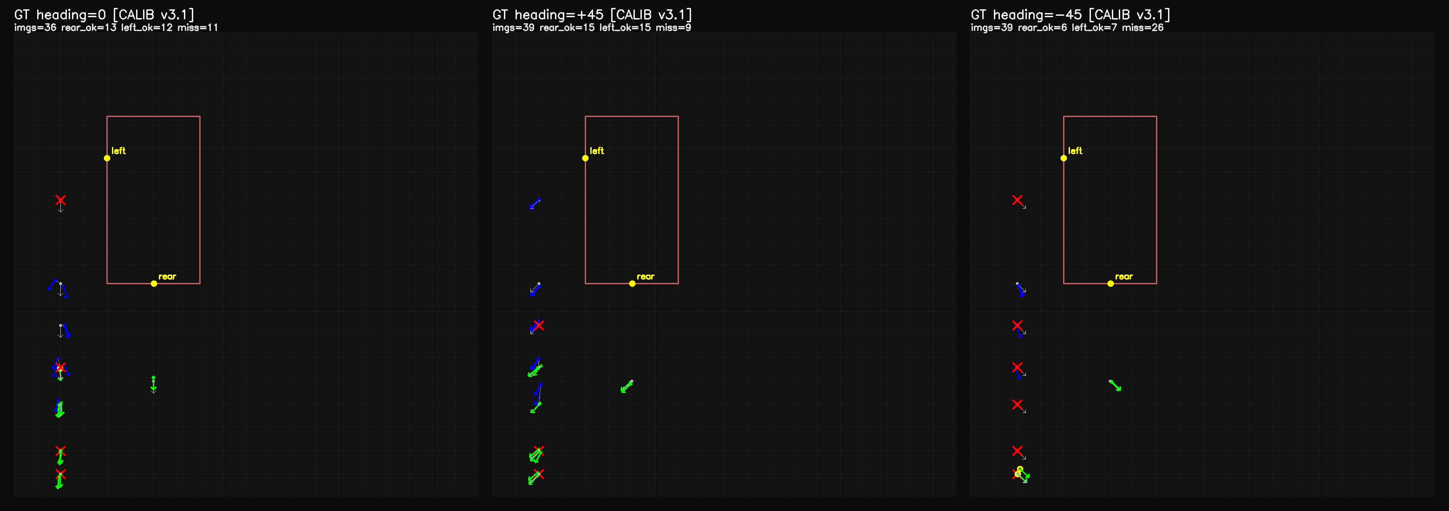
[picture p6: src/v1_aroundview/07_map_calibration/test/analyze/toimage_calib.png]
|  |  |

**8단계 파이프라인 중 7단계가 실기체에서 동작했다.** 캘리브레이션 → 탑뷰 합성 → 위치추정 → A\* 경로계획 → CAN 제어까지 이어졌다.

<div align="center">
<a href="https://youtu.be/o30saxUv7JM">

</a>
<br><sub>V1 실기체 테스트 — 어안 2뷰(좌 · 후방)로 마커를 추적하고 탑뷰 맵에 위치를 찍는다 &nbsp;·&nbsp; 이미지를 누르면 영상이 열린다</sub>
</div>

### 막힌 곳은 튜닝이 아니었다

<div align="center">

</div>

어라운드뷰는 **차량 바로 주변**을 보라고 달린 장치다. 그런데 휠체어는 그 밖에서 출발한다.
멀어질수록 마커가 화면에서 작아지고 렌즈 주변부로 밀려나, **캘리브레이션으로 메울 수 없는 구간이 남았다.**

보정을 아무리 정교하게 해도 소용없는 종류의 문제였다.

> **캘리브레이션은 왜곡을 펴는 것이지, 찍히지 않은 곳을 보이게 하지 못한다.**

그래서 **카메라를 움직이는 쪽에 실었다.** 대상까지의 거리가 항상 가까우면 이 문제 자체가 생기지 않는다.

---

## 4. V2 — 휠체어가 차를 본다

### 4-1. 공개 데이터셋이 안 통했다

공공 데이터셋으로 학습한 모델은 실차 영상에서 검출되지 않았다. **도메인 불일치를 자체 촬영·라벨링으로 해결**했다.

<div align="center">

<br><sub>도메인 데이터 추가 학습 전(v4, 좌)과 후(v5, 우). 같은 프레임에서 검출 0건 → 4건</sub>
</div>

| 버전 | 변경 | 결과 |
|---|---|---|
| `v1_merged` | 공공 5종 통합 | 번호판이 배경과 충돌해 억제됨 |
| `v2_ft` | 신형 번호판 fine-tune | plate 검출 **13 → 80 프레임** |
| `v3_ray` | 실차 도메인 데이터 추가 | 번호판 실영상 개선 |
| `v4_6cls` | 후미등 추가, 6클래스 재학습 | 아래 mAP50 |
| **`v5_poster`** | 실물크기 목업 60장 추가 | 포스터 환경 검출 **6배**, conf **0.26 → 0.89** |

자체 구축 라벨 — **실차 121장 + 실물크기 목업 60장**

| license_plate | car_emblem | door_handle | fuel_cap | tail_light | side_mirror |
|:---:|:---:|:---:|:---:|:---:|:---:|
| **.995** | **.974** | **.917** | .878 | .811 | .754 |

### 4-2. 번호판이 자가 된다

거리 센서 없이, **번호판 규격 335 × 155 mm가 국가 표준으로 고정되어 있다는 점**을 이용했다.

| 값 | 계산 | 제어에서의 의미 |
|---|---|---|
| **거리** | 핀홀 `D = H_real · f / h_px` | 얼마나 남았나 |
| **yaw** | 폭/높이 비율 `acos` + 꼭짓점 키스톤으로 부호 | 차가 얼마나 비스듬한가 |
| **bearing** | `atan((x_center − cx) / f)` | 차가 시야 어느 쪽인가 |

실영상 검증 — 실측 1.2 m 정면 → 추정 **1.20 m**, yaw ≈ 0

### 4-3. 9단계 주차

<div align="center">

</div>

거리 센서 하나로 끝나지 않는다. **카메라(IBVS) · 초음파 · IMU가 단계마다 번갈아 기준이 된다**. 시야로 맞출 수 있는 곳은 카메라가, 각도는 IMU가, 간격은 초음파가 담당한다.

> 위는 설계한 순서다. **자동으로 도는 것은 1·2단계까지다.** `AlignmentPlanner`
> (`guidance/common.py:175`)가 VISION(사이드미러 IBVS) → SONAR(측면 초음파 평행)
> 두 국면을 돌린다. 3단계부터는 단계를 잇는 시퀀서를 붙이지 못해 수동 조작으로 이었다.

### 4-4. 캐스터 휠 — 관측할 수 없는 상태

전동휠체어 앞바퀴는 **캐스터 휠(자유 회전)**이다. 직진 명령을 줘도 **바퀴가 이전에 틀어져 있던 방향으로 휘어 나간다.** 그리고 그 틀어짐을 읽을 센서가 없다.

관측 불가능한 상태를 추정하는 대신 **결과를 직접 측정하는 쪽**을 택했다. IMU로 실제 회전각을 읽어 목표에 도달할 때까지 보정하면, 바퀴 정렬과 무관하게 회전이 보장된다.

> 이 방식으로 V2에 구현한 것은 **직진 중 방위 유지**다(`experiments/straight_drive.py`).
> 회전각 도달까지 보정하는 폐루프는 V1에만 있다(`08_parking/tracker.py:188`, yaw 오차 데드존).

> 이 문제는 V1에서 이미 나타났다. 카메라를 옮긴다고 사라지는 문제가 아니었다.

### 4-5. Jetson Nano 4GB

휠체어에 실을 컴퓨터라는 제약 위에서 설계했으므로 탑재 가능성을 측정했다.

| 처리 속도 | 프레임당 추론 | RAM | GPU | 전력 | 온도 |
|---|---|---|---|---|---|
| **지속 15 FPS** (최대 22) | 42 ms | **3.55 / 3.96 GB** | 평균 35% | 5.8 W | 47~49 ℃ (팬 없음) |

모델 로드 구간에서 시스템이 프리징했는데, 원인이 스왑 부족(512 MB)임을 확인하고 4 GB로 확장해 해소했다.

---

## 5. 결과와 한계

| | |
|---|---|
| 차량 부위 6종 탐지 | mAP50 **0.995 ~ 0.754** |
| 자체 구축 라벨 | 실차 **121장** + 목업 **60장** |
| 도메인 학습 효과 | 검출 프레임 **6배**, conf **0.26 → 0.89** |
| 단안 거리 추정 | 실측 1.2 m → 추정 **1.20 m** |
| 엣지 실시간성 | Jetson Nano **15 FPS** / 5.8 W |
| V1 파이프라인 | 8단계 중 **7단계 실기체 동작** |
| 실기체 | AgileX TRACER (CAN) · JUVO B4 전동휠체어 |

### 단계마다 남은 문제

각 단계가 기대는 가정이 다르고 그중 몇은 아직 약하다.

| 단계 | 남은 문제 |
|---|---|
| 1. IBVS 초기 정렬 | 좌우로 진동하며 특징을 매칭하지 못하는 구간이 있다. YOLO를 올리며 메모리가 1 GB 늘어 **3.6 / 4 GB**까지 찼다 |
| 2. 초음파 평행 | 횡방향 간격은 잡히지만 **x축 정렬은 IBVS 오차가 크다** |
| 3 · 5 · 8. 직·후진 | 캐스터 휠 정렬에 따라 이동 방향이 휜다 (회전만 IMU로 보장) |
| 4. 70° 회전 | **고정값이라** 시작 위치가 달라지면 따라가지 못한다 |
| 6. IBVS 후방 정렬 | 좌측 초음파 2개 간격이 짧고 완전한 후방이 아니라 매번 같은 위치로 수렴하지 않는다 |
| 7. IMU 정면 회전 | 전방 초음파가 하나뿐이라 평행 여부를 알 수 없어 IMU 오차가 그대로 남는다 |

### V3 — 보지 않는 쪽으로

위 목록에서 **1·2·6은 시야에 의존하는 정렬**이고, **3·5·8은 관측 불가능한 바퀴 상태**에서 비롯된다.
개별 단계를 튜닝하는 대신 **시야에 의존하지 않는 측위**로 바꾸면 상당수가 함께 사라진다.

**UWB**를 검토 중이다. 오차 ±10 cm, 현대·기아가 디지털키에 이미 상용화, 카메라 대비 설치 위치·각도 제약이 적다.
시각 정보는 마지막 정밀 정렬에만 쓰는 구조다.

> **현재 조사와 장비 구매까지 진행했다. 실험은 시작하지 않았다.**

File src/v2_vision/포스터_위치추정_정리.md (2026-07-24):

# 포스터 위치추정 작업 정리 (2026-07-23~24)

포스터(실물크기 레이 목업) 환경에서 v5 학습 → 전 구간 위치추정 → 자동 검증까지.
README.md(전반), 거리추정_정리.md(거리·yaw·bearing 원리)와 함께 읽을 것.

## 무엇을 만들었나

1. **models/best_v5_poster.pt** — 포스터 60장(ray_poster.bin, POSTER_REPEAT=12 독립 소스)
   추가 학습. 포스터 환경에서 v4 대비 (포스터레이.MOV 2,513프레임 실측):
   plate 118→718프레임(conf 0.26→0.89) / mirror 4배 / tail 3.6배 / emblem 44배.
   ※ 실차·공공 성능 재검증은 아직 (레이영상 1~3 재실행 필요)
2. **scripts/pose_full_video.py** — 전 구간 연속 위치추정 + 미니맵 영상.
   원리: 검출 부위들의 bearing 후방교회법 + 번호판 yaw 절대위치(핀홀) 융합
   + 휠체어 물리 제한 + 가시성 제약. 출력: 영상/CSV/궤적 PNG.
3. **scripts/verify_pose.py** — 자동 검증 7종 (물리한계 2, 구역-위치 일관성 2,
   정상상태 정합, 재획득 수렴, 커버리지). 추정기 수정 후 반드시 이걸로 확인.
4. outputs/poster_compare/ — v4/v5 비교컷·비교영상, 궤적 그림, 포즈 CSV.

## 최종 검증 결과 (2026-07-24)

| 항목 | 결과 |
|---|---|
| 이동 ≤1.5m/s · 회전 ≤90°/s | 위반 0 |
| 후면구역⇒차뒤 · 측면구역⇒왼쪽밖 | 위반 0 |
| 정상상태 정합 (vs 번호판 물리모델) | RMS 0.04m |
| 관측공백 후 재획득 수렴 (2.5s 내 0.3m) | 4/4 성공 |
| 커버리지 (차가 보이는 프레임 중) | 64% (기준 65% — 아래 '남은 일' ③) |

## 핵심 발견 — 실차 전환 시에도 그대로 적용됨

1. **포스터 번호판은 장형(520×110)** — 단형(335×155) 아님! 정면 프레임 픽셀비 4.82로 확인.
   단형으로 계산하면 거리가 41% 과대. distance_video.py를 포스터에 쓸 땐 반드시
   PLATE_W_M/H_M/TRUE_AR override (pose_full_video.py 상단 참조).
   ※ 실차 레이("66라 5623")는 단형이므로 실차 복귀 시 override 제거할 것.
2. **목업은 다면 입체** (왼쪽면·후면 + 전면부 인쇄 확인). 측면 패널에 후미등
   옆모습까지 인쇄돼 있음 → "후미등 보임 = 후면"이 성립 안 함.
3. **면 판별에 쓸 수 있는 부위는 제한적**: 후면 증거 = 번호판·엠블럼만.
   측면 증거 = 손잡이·주유구만. (후미등은 측면에도, 미러는 돌출이라 뒤에서도 보임)
4. **영상의 ~32%는 차가 프레임에 없음** (21~40s, 52s 부근, 63~72s) — 비전 단독
   추정의 커버리지 상한. 안 보일 땐 LOST로 정직하게 표시 (낡은 위치 유지 금지).
5. **랜드마크 2개는 자세(x,y,θ) 미결정** → 그 프레임은 위치 동결이 정답 (억지로
   풀면 드리프트). 강한 근거 = 번호판+yaw 또는 랜드마크 3개 이상.
6. **물리 제한의 이동 예산은 "마지막 강한 관측부터의 경과시간"** 기준 — 매 프레임
   기준으로 걸면 공백 후 재획득을 못 따라감, 안 걸면 순간이동(65m/s 관측됨).

## 좌표계 (미니맵·궤적·CSV 공통)

번호판 중심 = 원점. X+ = 후면을 마주보고 오른쪽(=차의 오른쪽/조수석),
Y+ = 차 뒤쪽. 검증된 예: 촬영 동선 "왼쪽→후면→왼쪽"이 x<0→x≈0→x<0으로 재현됨.

## 남은 일

1. **포스터 줄자 실측 4개** → pose_full_video.py의 LANDMARKS 갱신:
   ① 인쇄 번호판 폭×높이(52×11cm 검증) ② 두 손잡이 중심 간 거리
   ③ 뒤 손잡이~뒷모서리 ④ 손잡이 높이. (현재 측면 좌표는 도면 추정 ±20cm)
2. **f 캘리브레이션** — 줄자로 잰 거리 1컷 촬영 → distance_video.py --calib
3. 부위 실측 크기(손잡이 폭·미러 높이)를 얻으면 박스크기→거리 추정을 추가해
   랜드마크 1~2개 프레임도 해결 가능 (커버리지 65%+ 목표)
4. 포스터레이_dist.mp4 재생성 (장형 반영 전 구버전이라 gitignore 처리해둠)
5. 도킹 제어 개발 시작: 진입점(차축 후방 1.5~2m) 계산 → 2단계 접근(곡선→직진),
   최종 정렬은 IBVS. 포즈 입력은 pose_full_video의 (x, y, θ) 그대로 사용
6. v5의 실차 성능 확인 (레이영상 1~3 재실행 — 포스터 특화로 깎였는지)

## 파일 목록

- scripts/pose_full_video.py / verify_pose.py — 본 작업 산출물
- outputs/distance/포스터레이_pose_full.mp4 — 최종 결과 영상 (LFS)
- outputs/poster_compare/ — 궤적_전구간.png, 궤적_번호판전용.png, pose_full.csv,
  pose_log.csv, cmp_frame*.jpg(v4|v5 비교컷), 포스터레이_v4_vs_v5.mp4(LFS)
- raw_videos/포스터레이.MOV — 원본 (LFS, 2,513프레임 84초)

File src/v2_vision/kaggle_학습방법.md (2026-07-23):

# Kaggle 재학습 가이드 (다음에 데이터 추가해서 학습할 때)

## 큰 그림
공공 6종 데이터(bin) + 내 레이 데이터(ray_all) + 포스터 데이터(ray_poster)를 합쳐 Kaggle T4에서 학습.
노트북: scripts/kaggle_finetune_v4.ipynb (6클래스 기준)
- ray_all.bin: 실차 촬영 121장 (RAY_REPEAT로 비중 조절)
- ray_poster.bin: 실물크기 포스터 촬영 60장, 2026-07 추가 (POSTER_REPEAT로 독립 조절.
  실전 테스트 환경이 포스터라 기본 12로 강하게 시작)

## 1. 로컬에서 .bin 만들기 (라벨 폴더가 원본)
새로 라벨링 끝난 폴더를 .bin으로 (ray_poster도 같은 방식):
    cd src/v2_vision/my_data/labeled
    cd ray_all && zip -r -q ../ray_all.bin . && cd ..
공공 6종 bin은 kaggle_upload/에 로컬 백업 보관 (Kaggle에도 업로드돼 있음).
둘 다 유실 시 raw_datasets/ zip을 SOURCES 파일명으로 개명하면 복원됨 (내용 동일, 2026-07-23 검증):
 car-door-handle.v4i→handle.bin / Side Mirror.v2→mirror.bin /
 license-plate-label.v5i→plate_old.bin / license plate.v1i→plate_new.bin /
 KIA Logo.v2i→logo.bin / Fuel Cap.v15i→fuel_cap.bin

## 2. Kaggle 업로드
- ray_all.bin (+ 새로 생겼으면 ray_poster.bin)을 데이터셋에 추가 (기존 데이터셋 있으면 거기에)
- .bin이라 data.yaml 자동압축해제 충돌 안 남

## 3. 노트북 실행
- Settings → GPU T4, Internet On
- Add Input: 공공 6종 bin 있는 데이터셋 + ray_all.bin
- scripts/kaggle_finetune_v4.ipynb 올리고 0번 셀부터 실행
- 확인: 0번(경로 3개 잘 찾나) / 3번(매핑·asis) / 4번(클래스 분포, tail_light 수, 레이 비중)

## 4. 학습 후
- best.pt 다운로드 → models/best_v5_xxx.pt (버전 올려서 저장)
- 검증: python3.11 scripts/test_video.py raw_videos/레이영상_3.mov <모델> 0.15
- README 성능 이력에 새 버전 추가

## 튜닝 손잡이 (노트북 1번 셀)
- RAY_REPEAT : 레이(실차)/후미등 비중. 약하면 올리고, 기존 클래스 무너지면 낮춤
- POSTER_REPEAT : 포스터 비중 (실차와 독립). 포스터 검출 약하면 올림, 실차·공공 무너지면 낮춤
- REHEARSAL_PER_CLASS : 공공데이터 양. 기존 클래스 흔들리면 올림
- EPOCHS : 새 클래스 추가 시 넉넉히(40), 이어받기면 적게(20)

## 함정 메모 (겪은 것)
- 클래스 추가 시 Roboflow는 알파벳순 → 전역 표준 순서로 재매핑 필요
- Roboflow auto-label(SAM3)은 세그멘테이션(폴리곤) 라벨 뱉음 → 박스 변환 필요
  (v4 노트북 3번 셀이 자동 변환함)
- v4 노트북은 여러줄 명령 복붙 시 zsh에서 # 주석 깨질 수 있음 → 한 줄씩 실행

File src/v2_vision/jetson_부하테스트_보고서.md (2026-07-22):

# Jetson Nano YOLO 부하 테스트 결과 보고

**테스트 일자**: 2026-07-22
**목적**: 휠체어 자동주차 시스템의 차량 부위 탐지 모델(YOLOv8n 커스텀, 6클래스)이
Jetson Nano에서 실시간 구동 가능한지 검증

## 1. 테스트 환경

| 항목 | 내용 |
|---|---|
| 보드 | NVIDIA Jetson Nano Developer Kit (4GB) |
| OS/SDK | JetPack 4.6 (L4T R32.6.1) |
| 소프트웨어 | Python 3.8.10, PyTorch 1.13 (CUDA 지원 빌드), Ultralytics YOLOv8 |
| 모델 | yolov8n 기반 커스텀 학습 모델 (best_v4_6cls.pt, 6.0MB) |
| 입력 | USB 웹캠, 추론 해상도 320px, 화면 표시 없이(headless) 구동 |
| 실행 스크립트 | src/v2_vision/scripts/live_camera.py |
| 전원 모드 | MAXN (10W, 4코어) + jetson_clocks 적용 |
| 스왑 | 기본 512MB → 4GB 파일 스왑 추가 (총 약 6GB) |

## 2. 구간별 부하 측정 결과

### ① 대기 상태 (YOLO 미실행, GUI 데스크톱만)

| 항목 | 측정값 |
|---|---|
| CPU | 코어당 0~8% |
| GPU (GR3D) | 0% |
| RAM | 약 2.2~2.6GB / 3.96GB |
| 온도 | CPU/GPU 약 40°C |
| 소비 전력 | 약 3.1~3.2W |

### ② 기동 구간 (모델 로드 + CUDA 초기화, 1회성)

| 항목 | 측정값 |
|---|---|
| 소요 시간 | 첫 프레임까지 약 43초 (환경에 따라 수 분) |
| CPU | 코어당 60~100% 버스트 |
| RAM | 2.6GB → 3.6GB로 급증 (약 1GB 추가 점유) |
| 소비 전력 | 최대 약 6.3W |
| 비고 | 스왑 512MB였던 초기 테스트에서는 이 구간에서 시스템 프리징 발생. **스왑 4GB 확장 후 해소** |

### ③ 실시간 추론 중 (정상 운용 상태, 약 2분 연속 측정)

| 항목 | 측정값 | 평가 |
|---|---|---|
| 처리 속도 | **지속 15 FPS** (구간에 따라 최대 22 FPS) | 카메라 공급 속도가 병목, 보드 여유 있음 |
| 프레임당 추론 시간 | 평균 42ms (이론상 ~23 FPS 여력) | |
| CPU | 코어당 20~60%, 포화 없음 | 여유 있음 |
| GPU (GR3D) | 5~63% 진동, 평균 약 35% | 여유 있음 (추가 연산 탑재 가능) |
| RAM | 3.55GB / 3.96GB에서 안정 유지 (증가 추세 없음) | 빠듯하나 안정 |
| 스왑 | 약 1.0~1.1GB / 6GB 사용, 완만 | 정상 |
| 온도 | CPU 47~49°C / GPU 46~48°C (팬 없음) | 스로틀링 여유 큼 |
| 소비 전력 | 평균 약 5.8W, 최대 6.4W | 아래 4절 참고 |

※ 요약 출력의 "평균 10.1 FPS"는 첫 프레임 초기화 43초가 포함된 수치로,
정상 운용 구간의 실효 성능은 15 FPS 이상임.

## 3. 결론

- **실시간 구동 가능 판정.** 추론 해상도 320 기준 지속 15 FPS를 유지했고,
  2분 연속 구동 동안 열·메모리·GPU 모두 안정 범위였음.
  저속 접근(도킹) 제어 용도로 충분한 프레임률.
- 현재 병목은 보드가 아니라 **웹캠의 프레임 공급(15fps)**.
  GPU 평균 사용률 35%로, 거리 추정 등 후처리 로직을 추가로 얹을 여유 있음.
- 기동 시 1회성 지연(약 40초~수 분)이 있으므로, 실제 운용 시
  시스템 부팅 후 미리 모델을 로드해두는 방식 필요.

## 4. 하드웨어 측 조치 요청/권고 사항

1. **전원**: 부하 시 소비 전력이 5.8~6.4W로, 마이크로USB(5V 2A=10W) 급전 시
   한계선 근처. 갑작스러운 전원 차단 방지를 위해 **DC 배럴잭 5V 4A 어댑터
   사용 권장** (J48 점퍼 장착 필요).
2. **저장 공간**: SD카드 26GB 중 96% 사용, 잔여 1.2GB. 방치 시 부팅 불능 위험
   → **용량 정리 또는 더 큰 SD카드로 교체 필요**.
3. **방열**: 현재 무팬 상태에서 48°C로 문제없으나, 여름철 실외/차내 환경이나
   장시간 연속 운용을 고려하면 **방열판+팬 장착 권장**.
4. (향후 성능 향상 옵션) TensorRT 변환 시 동일 모델로 추론 속도 2~3배 개선 가능
   — 추론 해상도 640 운용이 필요해질 경우의 카드로 보유.

## 5. 남은 검증 항목 (소프트웨어 측)

- 실제 차량(레이) 대상 검출 동작 확인 (본 테스트는 부하만 검증, 검출 0개는
  차량이 화면에 없었기 때문)
- 추론 해상도 640에서의 FPS 측정 (원거리 번호판 검출용)
- 젯슨 카메라 기준 초점거리 캘리브레이션 (거리 추정 로직 이식 시)

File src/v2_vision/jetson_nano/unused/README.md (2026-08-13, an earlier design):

# unused — 지금 안 쓰는 코드

현 워크플로우에서 대체된 코드 보관소. 지워도 되지만, 다시 꺼내 쓸 상황이
명확한 것들이라 이력 겸 남겨둠.

## live_camera.py
카메라 단독 실행 + YOLO 부하(FPS) 테스트 스크립트. `hardware/` 공용 계층이
생기기 전의 독립 스냅샷이라 파이프라인 코드를 자체 보유.
→ **대체:** `main.py --no-servo` (카메라만 테스트) 가 같은 역할을 함.
꺼내 쓸 상황: 순수 FPS 통계(평균/최대 추론시간 요약)가 필요한 부하테스트.

## test_sample.py
초음파+서보 수동 조작 curses 툴 (A/D/W/S 서보, 텔레메트리 표시).
`hardware/` 이전의 독립 스냅샷.
→ **대체:** `main.py` 가 같은 화면+조작에 비전까지 얹어서 대체함.
꺼내 쓸 상황: **카메라 없이** ESP32만 빠르게 점검하고 싶을 때 (main.py는
카메라가 없으면 안 뜸).

## joystick/
휠체어 주행 방향(0/90/180/270 각도 + stop) 제어용 코드. `keyboard.py`로 방향키 →
`joystick_controller.py` → `serial_link.py`로 시리얼 전송까지는 동작하지만,
**이 프로토콜을 받아줄 펌웨어가 아직 없음** (지금 연결된 ESP32는 `ultrasound/sample.ino`이고,
이건 초음파+서보 프로토콜만 처리함 — 주행 모터 명령은 무시됨).

실제 "조이스틱" 역할(방향 조종)은 서보 액추에이터(main.py 수동 / guide.py --drive 자동)가
대신하고 있어서, 이 폴더의 프로토콜은 당장 필요 없음. 실제 주행 모터/보드가 준비되면
그때 다시 꺼내 쓰거나, 새 펌웨어에 맞게 프로토콜을 고쳐서 씀.

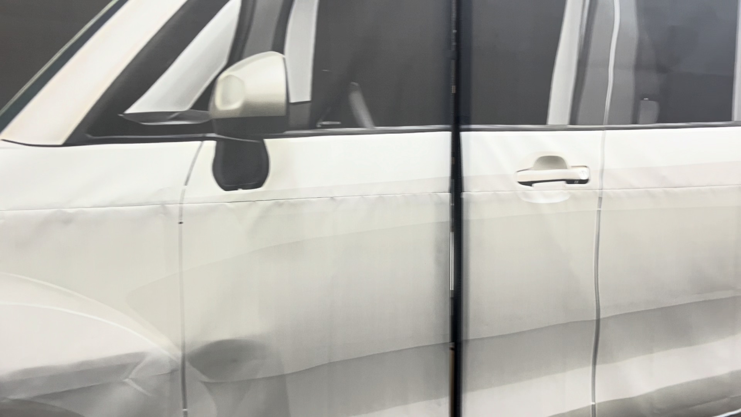
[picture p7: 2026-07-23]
src/v2_vision/my_data/labeled/ray_poster/train/images/1_mov-0010_jpg.rf.KtnxheDmjYH3R3RTRx1q.jpg

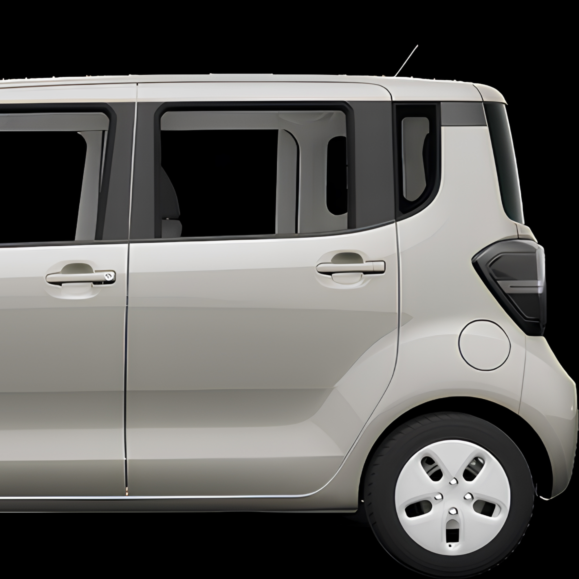
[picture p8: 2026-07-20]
src/v2_vision/my_data/labeled/ray_poster/train/images/Frame 1_jpg.rf.wUMPoHUtx5qrxzuRurDE.jpg

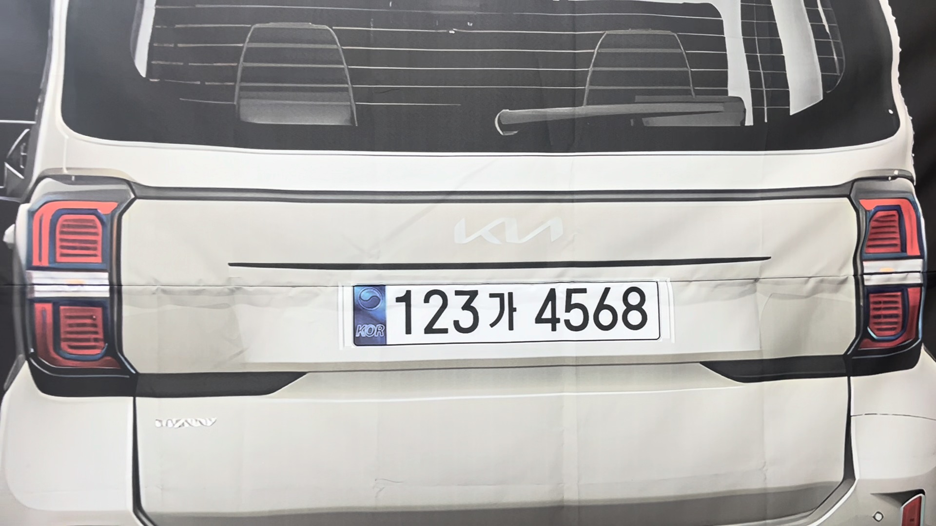
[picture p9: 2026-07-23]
src/v2_vision/my_data/labeled/ray_poster/train/images/3_mov-0002_jpg.rf.EDP4rNr58UZJW53RC7dJ.jpg

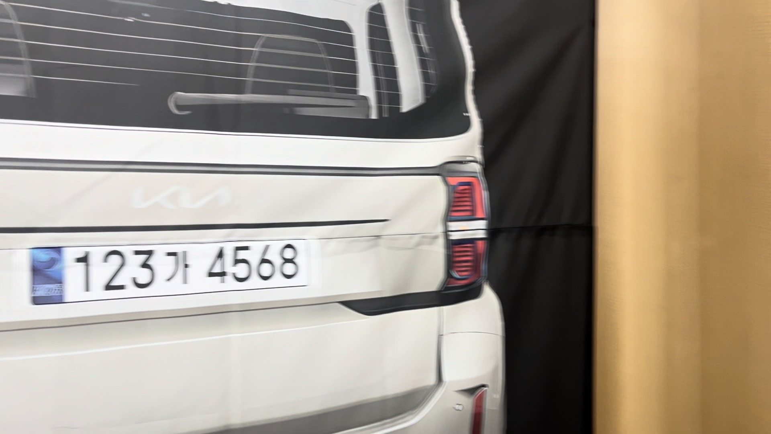
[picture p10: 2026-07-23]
src/v2_vision/my_data/labeled/ray_poster/train/images/3_mov-0000_jpg.rf.0cs9u6hFa06FYxZIv3Ti.jpg

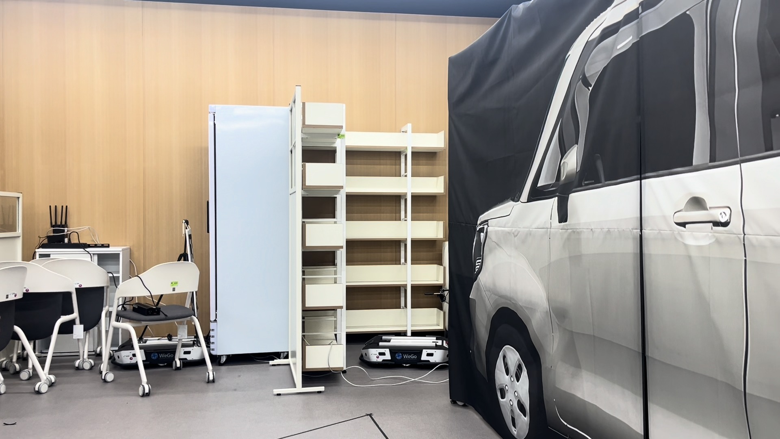
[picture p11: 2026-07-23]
src/v2_vision/my_data/labeled/ray_poster/train/images/3_mov-0019_jpg.rf.uSmhFmeutnug2jVXIZx2.jpg

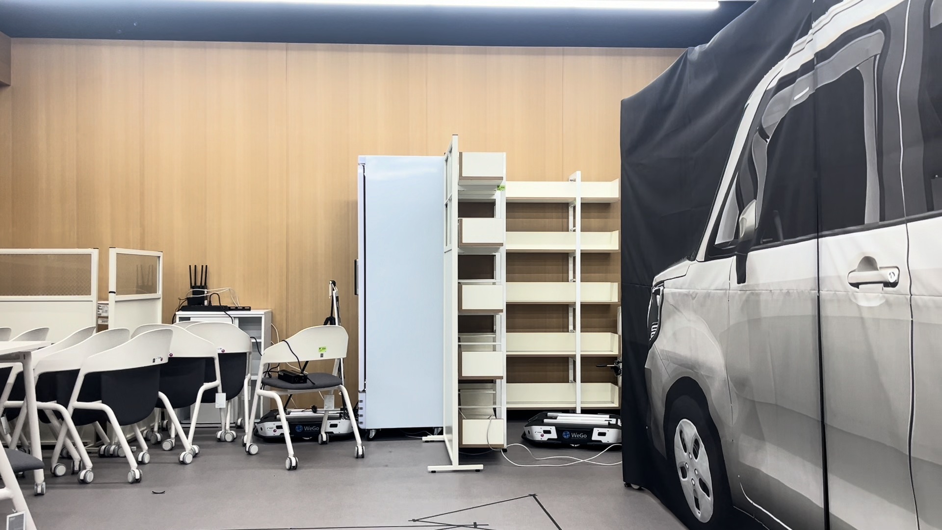
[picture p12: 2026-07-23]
src/v2_vision/my_data/labeled/ray_poster/train/images/3_mov-0016_jpg.rf.ZFJjFS4eA8oSICpu8xyB.jpg

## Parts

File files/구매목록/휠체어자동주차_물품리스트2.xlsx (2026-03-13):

번호 | 상품코드 | 상품명(옵션명) | 제조사 | 링크 | 수량 | 단가(VAT포함) | 합계금액 | 배송비 | 구매옵션
1 | 14497608 | 18650 배터리용 홀더 직렬 2구 스위치+전선 타입 [LIBH-BCS-2] | SMG | https://www.devicemart.co.kr/goods/view?no=14497608 | 1 | 1210 | 1210 | -
2 | 1327955 | RGB 4P 절연전선 1미터 [NW3-LC006] | NW3 | https://www.devicemart.co.kr/goods/view?no=1327955 | 8 | 550 | 4400 | 2700
3 | 2621 | E/C 10V 2200uF (105℃) | SAMYOUNG | https://www.devicemart.co.kr/goods/view?no=2621 | 10 | 176 | 1760 | -
4 | 24167 | [LD41] 12*500 휘어지는 사각만능기판 / 양면 | 거상인 | https://www.devicemart.co.kr/goods/view?no=24167 | 2 | 5060 | 10120 | -
5 | 1280 | WCR 10Ω 5W | 바로전자 | https://www.devicemart.co.kr/goods/view?no=1280 | 10 | 198 | 1980 | -
6 | 13204012974 | IRLZ44N TO-220 10 개 | - | https://smartstore.naver.com/pickngoms/products/13204012974?nl-au=25179ef8a2f4465285674adb3a19421e&nl-query=IRLZ44N | 1 | 13650 | 13650 | - | 01 IRLZ44N
7 | 9750256002 | DC변환 강압회로 5A 컨버터 XL4015 | 리틀브릿지 | https://smartstore.naver.com/littlebridge/products/9750256002?nl-ts-pid=jj%2FZssqqQ1ciiuxHLU0-271499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 | 1 | 2900 | 2900 | 3000
8 | 10744649710 | IR LED 칩 이미터 DC1.5-1.7V 보안용 20mm 스타 플래틴 베이스 포함 무료 배송 1W 3W 5W 850nm 5 개 | - | https://smartstore.naver.com/amuseby_/products/10744649710 | 2 | 11500 | 23000 | - | 01 1W 1chip
9 | 12931536949 | 사각 쌍안 적외선 이미징 필터 좁은 밴드패스 850nm 렌즈 4.5mm 6.2mm 8.2.0mm | - | https://smartstore.naver.com/jk15_/products/12931536949?nl-au=1c82b91e9dfa4df08c590c1b1610b806 | 2 | 9040 | 18080 | - | 07 square6.2x6.2x0.55mm
 |  |  |  |  |  |  |  |  | 총액
 |  |  |  |  |  |  | 77100 | 5700 | 82800

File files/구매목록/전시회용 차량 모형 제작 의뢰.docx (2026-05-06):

전시회용 차량 모형 제작 의뢰

차종: 기아 레이(실물 크기, 내부 구현 x, 도면 제공)

재질: 우드락, 종이, 나무

특징

- 기아 레이 차량과 사이즈만 같으면 됨

- 내부 구현(차량 문 개폐x) 필요 없고, 트렁크만 열리고 닫히면 됨

예시 사진

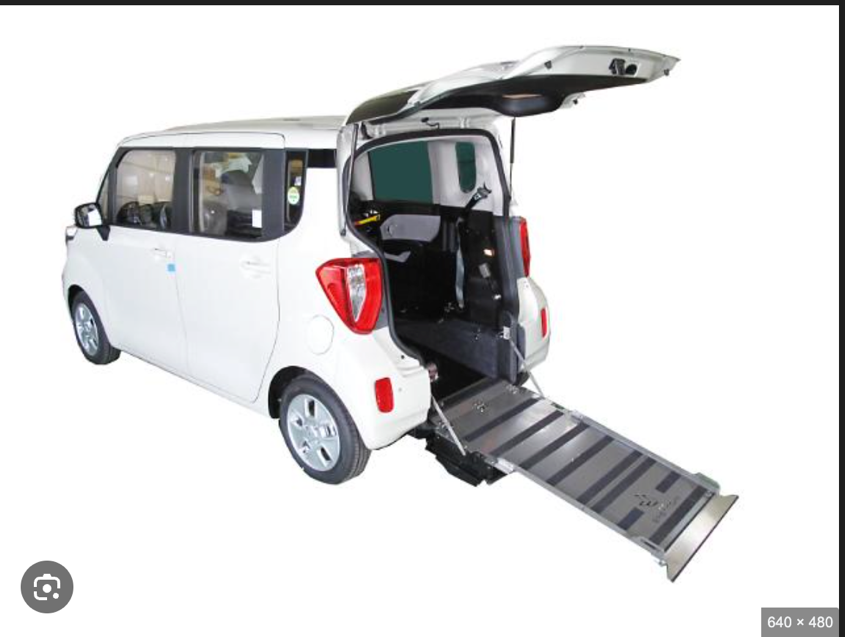
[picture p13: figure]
차량, 바퀴, 육상 차량, 교통이(가) 표시된 사진 AI 생성 콘텐츠는 정확하지 않을 수 있습니다.
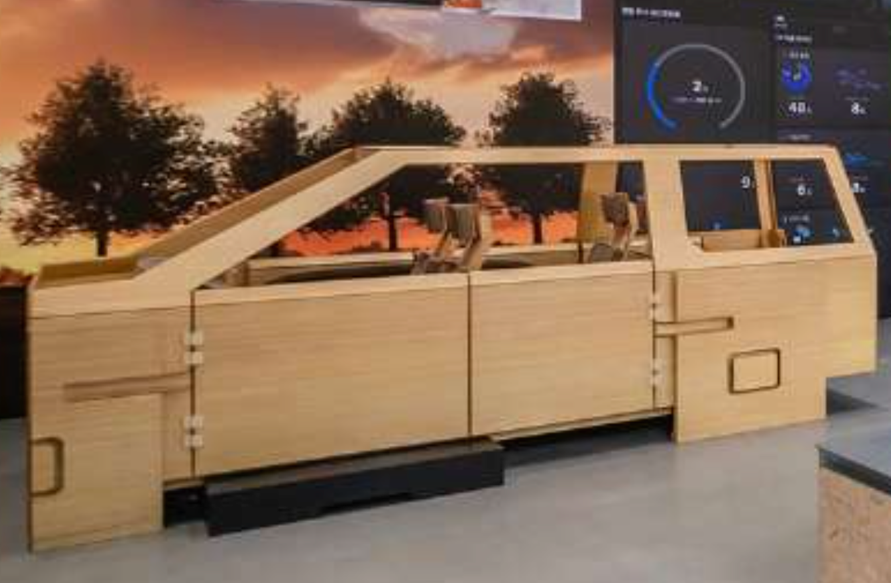
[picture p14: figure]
자동차, 바닥, 실내, 디자인이(가) 표시된 사진 AI 생성 콘텐츠는 정확하지 않을 수 있습니다.

\

일당 25만원 이상의 목수,

MDF합판 10mm이상 + 필름지로 마감

1220mmx2440x 12mm: 개당 15,455원

무너질 수 있으니 각재로 고정

각재: 30mmx30mmx1700mm(높이) : 개당 2,630원

1. 도면 그리기

2. 공방 및 목공소에 의뢰

3. 안에 들어가는 실린더 및 경첩으로 고정

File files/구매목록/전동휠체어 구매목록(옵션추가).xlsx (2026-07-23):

제품명 | 구매주소 | 수량 | 개당가격 | 택배비 | 총 가격 | 옵션
리튬이온충전기 | https://smartstore.naver.com/angelbtr/products/2365016586?nl-ts-pid=jEtn7sqosZqdB5cBYDK-135832 | 1 | 9000 | 3500 | 12500 | X
SEN-22857 BNO086 | https://smartstore.naver.com/muzelian/products/13373904277?nl-query=BNO086&nl-ts-pid=jEtS4wqX5mhsslH0oAh-456372 | 1 | 56620 | 0 | 56620 | X
Logitech C920 PRO HD WebCam | https://smartstore.naver.com/daldreamcom/products/6275529777?nl-query=logitech%20camera&nl-au=144de71bcf8a4ccd84ba87203e244a86 | 1 | 68300 | 0 | 68300 | C920(필수)
클리어겔 양면테이프 | https://smartstore.naver.com/3m_diy/products/11705611894?nl-ts-pid=jEax5dqosZreR5cBt3G-359643 | 2 | 11900 | 0 | 23800 | 01_클리어겔 양면테이프 30mmX3m (필수)
 |  |  |  |  | 0
 |  |  |  |  | 0
 |  |  |  |  | 0
 |  |  |  |  | 0
 |  |  |  | 전체가격 | 161220

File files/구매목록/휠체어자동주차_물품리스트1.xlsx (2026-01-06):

구분 | 비고 (용도) | 품목명 | 규격/옵션 | 수량 | 단가 | 배송비 | 합계 | 구매처(링크) | 진행상황 | 방식
1 | 조이스틱 제어 | 서보모터 | MG996 | 2 | 2980 | 3000 | 8960 | https://smartstore.naver.com/openhw/products/2432296643?nl-query=%EC%84%9C%EB%B3%B4%EB%AA%A8%ED%84%B0&nl-au=9dd3845532a34c2d916590ef568e27a0 | 주문 전
2 | 전원부 | 18650 리튬이온 배터리 | 3000mA | 2 | 4500 | 3000 | 12000 | https://smartstore.naver.com/lighthunter/products/10966261696?nl-au=2026c869717e4f30aee8e345b47eaf32 | 주문 전
3 | 전원부 | 마이크로 USB POWER LOGIC 은행 모듈 | V8 | 1 | 10380 | 0 | 10380 | https://smartstore.naver.com/globelle/products/12388764477?nl-au=b4d4c09a0f7c416a8c1345b9318b7016 | 주문 전
4 | 어라운드 뷰 구현 | 광각 웹캠 (어안) | 180도 시야각, USB출력(후처리는 PC에서) | 4 | 95040 | 0 | 380160 | https://smartstore.naver.com/raili/products/12733637134?nl-au=ebcf9ea782814216acbf48a5f87cb5eb&nl-query=%EA%B4%91%EA%B0%81+%EC%9B%B9%EC%BA%A0 | 배송 완료 | 1. USB로 입력받은 4개의 카메라 스트림을 받는다. (Camera 1,2,3,4 OpenCV로 읽음) | 2. 체커보드를 활용해 네 카메라의 왜곡 보정한다. | 3. 왜곡된 fisheye영상을 직선으로 보이게 변환하는 과정 거침(왜곡보정) | 4. 탑뷰를 보기 위해 이미지 처리 영역에서 좌표 보정함
5 | 어라운드 뷰 구현 | 삼각대 | 1.3m | 4 | 18000 | 2500 | 74500 | https://smartstore.naver.com/mkit/products/758607979?nl-au=c2a16255d7334fba9466dd8de105cda7 | 배송 완료
6 | 웹캠 -> PC 연결 | USB 3.0 연장 케이블 | 2m | 2 | 7700 | 2500 | 17900 | https://brand.naver.com/basicgear/products/11988028168?nl-query=usb%20%EC%97%B0%EC%9E%A5%202m&nl-au=8624a2de785349ce850aa55e35bfde64 | 배송 완료
 |  |  |  |  |  | 합계 | 486000

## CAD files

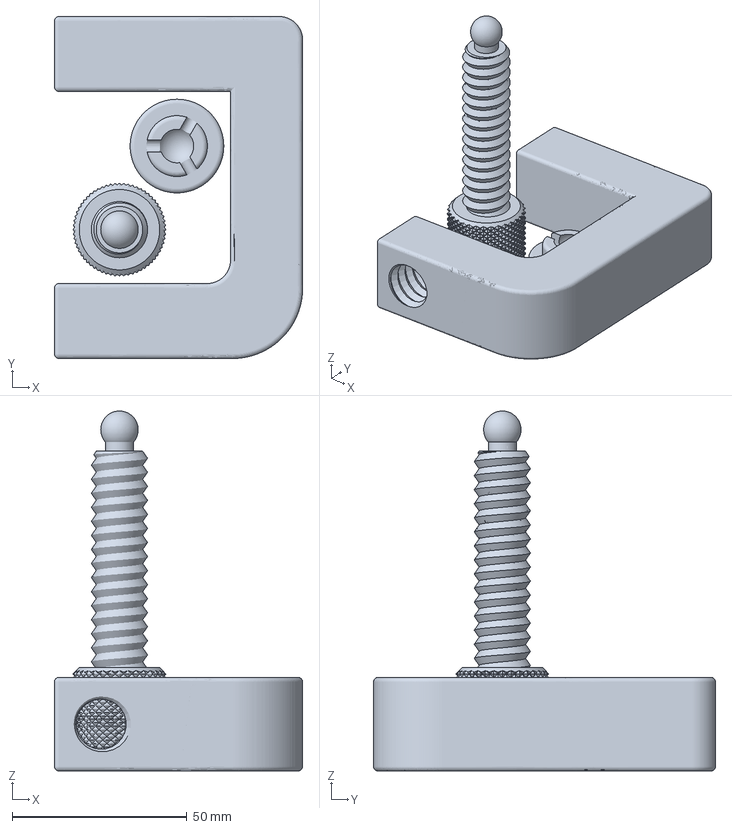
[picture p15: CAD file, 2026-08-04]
files/models/clamp.3mf
71.0 x 97.8 x 103.0 mm

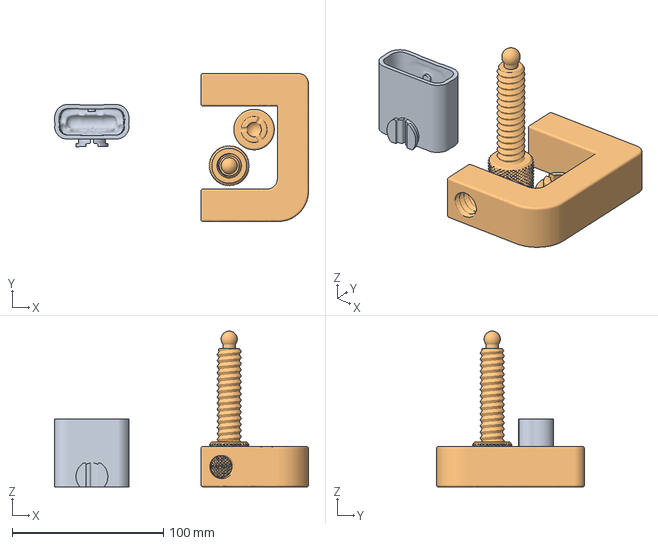
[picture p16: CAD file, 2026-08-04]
files/models/C920_Wall_Mount_-_Bambu.3mf
167.9 x 97.8 x 103.0 mm
C920_Mount
G-Clamp deeper strong.stl

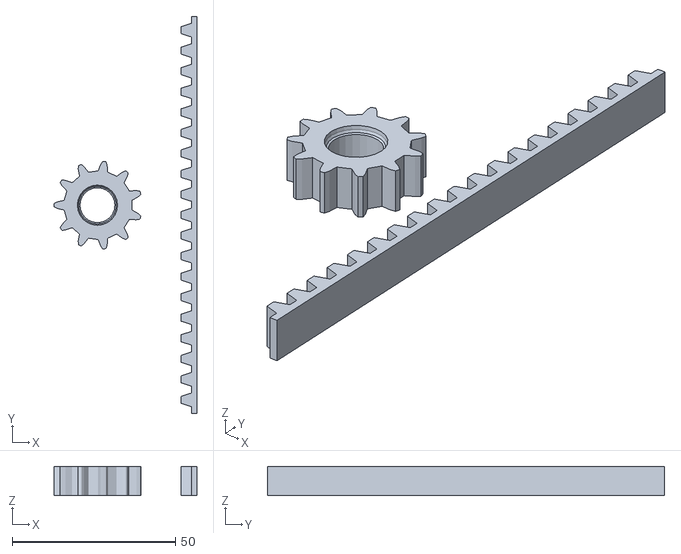
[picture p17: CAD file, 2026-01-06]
files/models/gear-and-rail-to-it.stl
43.7 x 121.5 x 9.00

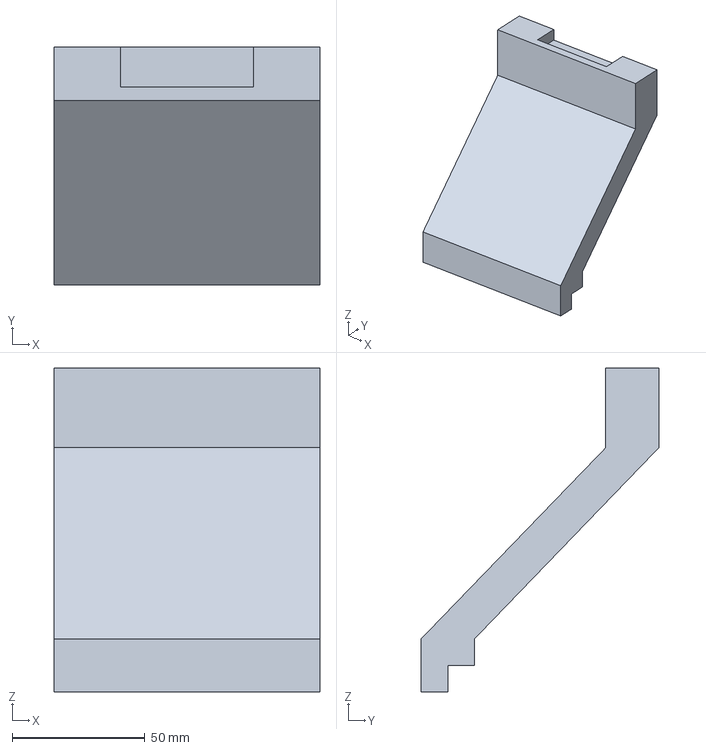
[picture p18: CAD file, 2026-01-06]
files/models/test1.3MF
100.0 x 89.5 x 121.9 mm

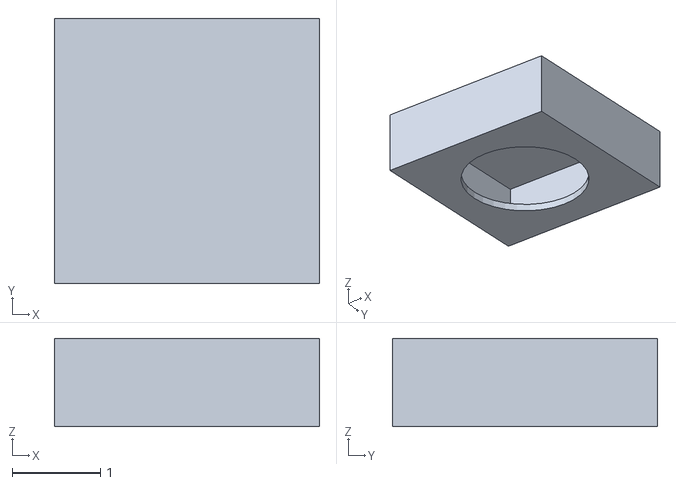
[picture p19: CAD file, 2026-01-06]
files/models/Untitled.stl
3.00 x 3.00 x 1.00

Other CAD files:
files/models/cube.gcode.3mf

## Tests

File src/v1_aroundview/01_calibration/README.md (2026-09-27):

# 01_calibration — 카메라 왜곡계수

체커보드를 촬영해 왜곡계수를 뽑고, 그 값을 Left·Rear 코드에 적용한다.

| 파일 | 하는 일 |
|---|---|
| `calibration.py` | 캘리브레이션을 돌려 왜곡계수를 반환 |
| `angle_left.py` · `angle_rear.py` | 왜곡계수를 적용해 ArUco 마커 각도를 반환 |

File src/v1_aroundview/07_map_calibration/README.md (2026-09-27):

# 07_map_calibration — 맵 오차 보정

| 파일 | 하는 일 |
|---|---|
| `main.py` | `c` 로 위치 보정, `a` 로 각도(원점·방위) 보정 |
| `backup_weight.py` | JSON 가중치로 오차 보정 |
| `outlier.py` | 튀는 값 제거 |

> **여기서 막혀 V1 을 중단했다.** 가중 보정은 쓸 만했지만 튀는 값을 잡는 쪽을
> 끝내지 못했다. 중단 사유는 [../README.md](../README.md) 참고.

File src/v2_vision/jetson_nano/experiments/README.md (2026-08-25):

# experiments — IMU 직진 유지 실험

캐스터(앞바퀴)가 매번 다른 방향으로 틀어져 있어서, 조이스틱을 정확히 앞으로 밀어도
휠체어가 휘어 나간다. 이 폴더는 그 문제만 따로 떼어내 IMU(MPU6050)로 잡는 실험이다.
카메라/YOLO를 안 쓰므로 3초면 뜨고, 시리얼만 있으면 돌아간다.

```bash
cd src/v2_vision/jetson_nano
python3 experiments/straight_drive.py
```

## 조작

시작하면 IMU yaw 캘리브레이션이 자동으로 돈다(자이로 0점 잡기). **그 몇 초 동안만
휠체어를 가만히** 두면 되고, 그 뒤로는 아래 키가 전부다.

| 키 | 동작 |
|---|---|
| `W` / `S` | 전진 / 후진 (방위각을 유지하며 간다) |
| `A` / `D` | 좌 / 우회전 — 의도된 회전이므로 보정하지 않음 |
| `SPACE` | 정지 |
| `I` | **기준 방위각 고정 / 해제** |
| `Q` | 종료 (조이스틱 중립 복귀 후) |

기준 방위각(= 맞추려는 방향)은 두 가지 방식으로 정해진다.

- **평소**: `W`/`S`를 누른 그 순간의 방위각. 그 구간 동안 그 방향을 유지한다.
  `A`/`D`로 돌리면 기준이 사라지고, 다시 `W`를 누르면 새 방향으로 잡힌다.
- **`I`로 고정했을 때**: 그 순간의 방위각을 못박는다. 이후 `A`/`D`로 아무리 돌려놓아도
  `W`를 누르면 **무조건 그 방위각으로 되돌아온다**(50° 벗어난 상태에서 약 7초).
  다시 `I`를 누르면 해제.

보정 ON/OFF·부호·yaw 켜기는 전부 자동이라 누를 키가 없다.

---

## 원리

### 무엇을 재고 무엇을 움직이나

- **잰다**: ESP32가 보내주는 `yaw`(누적 방위각, °)와 `gyro_z`(회전 각속도, °/s).
- **움직인다**: 조이스틱을 물고 있는 서보 2축. `x`가 좌우(조향), `y`가 전후(속도).
- **부호 규약(실측)**: 서보 `x`를 중립 87보다 **키우면 왼쪽**, 그때 `yaw`가 증가하고
  `gyro_z`가 양수. **전진/후진 모두 같다** (아래 "후진 부호" 절 참고).

보정은 **`x`(조향)만 건드린다.** `y`(전후 속도)는 프리셋 그대로 둔다.

### 왜 캘리브레이션이 아니라 피드백인가

캐스터가 어느 쪽으로 틀어지는지는 직전에 어떻게 움직였느냐에 따라 매번 달라진다
(실측 -1.6 ~ +4.9°/s, 방향도 뒤집힌다). 미리 "이만큼 틀어지니 이만큼 상쇄" 하는
상수를 구해둘 수가 없다. 그래서 **매 순간 실제로 얼마나 돌고 있는지를 재서 그만큼
되받아치는** 폐루프로 간다. 틀어짐의 패턴을 몰라도 되는 게 이 방식의 핵심이다.

### 제어식

이동 중(`W`/`S`)일 때 매 루프(~33Hz) 아래를 계산한다.

```
yaw_err  = yaw - yaw0                            # 기준에서 얼마나 벗어났나 (°)

# ① 방위 오차 → 목표 회전속도 (°/s)
rate_tgt = 0                    if |yaw_err| <= 1.0      (데드밴드)
         = -yaw_err / 1.5       그 밖에                   (CORR_TAU=1.5초)
rate_tgt = clamp(rate_tgt, ±10)                          (CORR_RATE_MAX)

# ② 목표 회전속도 vs 실제 회전속도 → 조향량
rate_err = rate_tgt - gyro_z
bias    += 0.8 * rate_err * dt                           (CORR_KI, ±13 제한)
u        = 0.4 * rate_err + bias                         (CORR_KR)

# ③ 데드존 보상
comp     = 4.0 * min(|u| / 1.5, 1)                       (CORR_DEADZONE / KNEE)
corr_x   = clamp(u + sign(u) * comp, ±13)                (CORR_MAX_DEG)

서보 x 목표 = 87 + corr_x     (램프가 83°/s로 접근)
```

**① 오차를 "속도 목표"로 바꾸는 이유.** 오차에 비례해 서보를 꺾는 단순 P제어는 반드시
좌우로 진동한다. 오차가 0이 되는 순간에도 휠체어는 관성으로 계속 돌고 있어서 반대편으로
넘어가고, 그러면 또 반대로 꺾기 때문이다. 실측으로 잡힌 장면이 이것이다 —
**오차 +1.2°(거의 복구)인데 자이로는 -17.7°/s**(맹렬히 돌아가는 중).
목표를 "각도"가 아니라 "지금 내야 할 회전속도"로 두면, 오차가 줄수록 목표 속도도
같이 줄어서 **스스로 감속**한다. 1.5초에 걸쳐 되돌리는 완만한 값이라 급하게 꺾지 않는다.

**② 자이로가 브레이크다.** 목표 회전속도와 실제 회전속도의 차이로 조향량을 정하므로,
이미 그쪽으로 충분히 돌고 있으면 더 밀지 않는다. 진동이 사라지는 지점이 여기다.

**② 적분항(`bias`)이 틀어짐을 학습한다.** 캐스터가 만드는 틀어짐은 한 구간 동안은
거의 일정하다. 그걸 이기려면 조향을 **계속** 물고 있어야 하는데, 비례항만으로는
오차가 남아야 힘이 나오므로 결국 **비뚤어진 채로 평행하게 가버린다**(시뮬에서 6°에
멈춤). 적분항이 "이 캐스터를 이기는 데 필요한 편향"을 주행 중 쌓아 물고 있어서
오차가 0으로 수렴한다. 화면의 `(학습 -5.2°)`가 이 값이다.

**③ 데드존 보상.** 조이스틱은 작게 밀면 아예 안 먹는다 — 실측으로 **편향 4.5°는
0.9초 동안 yaw가 한 자리도 안 변했고, 13°에서 갑자기 -18°/s**가 나왔다. 그래서 최소
편향을 얹어 반응하는 구간까지 끌어올린다. 단, 계단식으로 얹으면 `u`가 0을 지날 때
좌↔우로 튀므로 `|u|`가 1.5에 이를 때까지 서서히 얹는다.

### 통신 끊김 대비

ESP32 텔레메트리는 **평균 3Hz, 최대 1.01초 공백**이다. 그 사이 같은 값이 계속 오므로
"새 값인지"를 구분해야 한다(`yaw != 직전 yaw`). 두 곳에 쓴다.

- **적분 정지** — 새 값이 0.45초 넘게 안 오면 `bias`를 쌓지 않는다. 눈 감고 쌓으면 폭주.
- **보정 페이드** — 같은 조건에서 `corr_x`를 0.4초에 걸쳐 0으로 뺀다. 안 그러면
  1초 공백 동안 최대로 밀어서 8°가 그냥 넘어간다.

### 기준 방위각을 "새 값"으로 잡는 이유

키를 누른 순간의 `yaw`는 최대 1초 묵은 값이다. 그대로 기준으로 삼으면 시작하자마자
없는 오차가 생긴다(실측 +1.8°). 그래서 키를 누르면 바로 잡지 않고 **새 샘플이 오고
직전 회전이 잦아든 뒤**(|gyro_z| < 4°/s, 최대 1.2초 대기) 잡는다. 화면에
`기준 방위각 잡는 중...`이 잠깐 뜨는 게 이 구간이다.

`W`/`S`를 연타해도 기준은 다시 잡지 않는다(누적된 오차를 용서하게 되므로).
상태가 실제로 바뀔 때만 잡는다.

### 안전 장치

- **전방 30cm 미만이면 자동 정지** (전진 중에만). 단 초음파 전원이 꺼져 있으면 무력.
- **기준에서 30° 넘게 벗어나면 자동 정지.** 보정만 놓으면 휠체어가 비뚤어진 채로
  계속 간다(실측: 12초 동안 78°까지). 그만큼 벗어났다는 건 뭔가 잘못됐다는 뜻이다.
  `I`로 고정한 상태에선 `A`/`D`로 돌린 뒤라 크게 벌어진 채 출발하는 게 정상이므로,
  절대값이 아니라 **"출발할 때보다 30° 더 벌어졌는가"** 로 판단한다.
- **어떤 경로로 끝나든 조이스틱 중립 복귀** (`Q`, Ctrl-C, 예외 전부).
- 서보는 한 번에 튀지 않고 **83°/s로 램프**되어 접근한다(브라운아웃 방지).

---

## 상수

`straight_drive.py` 상단. 튜닝값은 실측 로그로 만든 플랜트 모델에 게인 스윕을 돌려
골랐고, 조향 권한이 실측의 절반~2배로 변해도 견디는 값이다.

| 상수 | 값 | 뜻 |
|---|---|---|
| `CORR_TAU` | 1.5초 | 방위 오차를 이 시간에 걸쳐 되돌린다 (작을수록 공격적) |
| `CORR_RATE_MAX` | 10°/s | 목표 회전속도 상한. 평소엔 3~5°/s만 쓰고, 고정 방위각 복귀에서만 여기까지 |
| `CORR_KR` | 0.4 | 회전속도 오차 1°/s당 서보 x |
| `CORR_KI` | 0.8 | 틀어짐 학습 속도 |
| `CORR_DEADZONE` / `KNEE` | 4.0 / 1.5 | 데드존 보상량 / 서서히 얹는 구간 |
| `CORR_MAX_DEG` | 13° | 보정 상한 (= 풀 회전 수준) |
| `CORR_DEADBAND_DEG` | 1.0° | 이 안쪽이면 되돌리지 않고 회전속도 0 유지만 |
| `CORR_STALE_S` / `FADE_S` | 0.45 / 0.4초 | 끊김 판정 / 보정을 빼는 시간 |
| `CORR_ABORT_DEG` | 30° | 이만큼 더 벌어지면 자동 정지 |
| `REF_SETTLE_RATE` / `MAX_WAIT` | 4°/s / 1.2초 | 기준 방위각을 잡는 조건 |

## 실측값 (2026-08-25)

| 항목 | 값 | 비고 |
|---|---|---|
| 조이스틱 중립 | x 87, y 85 | 90/90이 아님 |
| 전진 / 후진 프리셋 | (87, 45) / (87, 115) | y 편향 40 / 30 |
| 좌 / 우회전 프리셋 | (100, 78) / (72, 78) | x 편향 +13 / -15 |
| 조향 데드존 | 편향 4.5° 무반응, 13°에서 -18°/s | 매우 비선형 |
| 캐스터 드리프트 | -1.6 ~ +4.9°/s | 방향은 직전 움직임에 따라 바뀜 |
| IMU 정지 드리프트 | 12초에 0.000° | 펌웨어 deadband |
| 텔레메트리 주기 | 평균 3Hz, 중앙값 0.25초, **최대 1.01초** | 병목 |
| 부호 규약 | 서보 x + (좌) → yaw 증가, gyro_z 양수 | **전진/후진 동일** |

## 한 번 틀렸던 것 — 후진 부호

"후진에선 조향이 반대"라고 믿고 후진에만 부호 반전을 넣었던 시기가 있었다. **틀렸다.**
전 로그에서 서보 편향 방향과 실제 yaw 변화를 대조해보면 전진/후진 모두 x+(좌) →
yaw 증가로 같다 (후진 +11.2° 편향에 +14.2°/s). 반전을 넣었던 건 그때 전역 부호가
반대여서 우연히 맞아 보였던 것이고, 전역 부호를 고친 뒤에도 반전이 남아 후진만
이중으로 뒤집혀 폭주했다 (110532 로그: 왼쪽으로 치우쳤는데 왼쪽 최대로 밀어 8°→31°).

자이로로 실제 회전을 재서 맞추는 구조에선 방향별 반전이 애초에 필요 없다.
부호가 의심되면 감으로 뒤집지 말고 로그에서 `cmd_x`와 `yaw` 변화를 대조할 것.

## 기록

`experiments/logs/drive_<시각>.csv` (10Hz, 1초마다 flush — 강제종료해도 남는다).
`logs/`는 `.gitignore` 처리되어 있다.

분석에 중요한 열:

- `yaw_err` — 기준 방위각에서 얼마나 벗어났나 (이게 작게 유지되면 성공)
- `rate_tgt` vs `gyro_z` — 목표 회전속도를 실제로 따라가고 있나
- `bias` — 캐스터 틀어짐을 얼마나 학습해서 물고 있나
- `corr_x` / `cmd_x` — 보정량과 실제 서보 명령 (중립 87 기준)
- `lock` — `I`로 기준을 고정한 상태였나
- `echo_x` / `echo_y` — ESP32가 되돌려준 실제 서보 위치 (명령이 먹었는지 확인용)

## 남은 문제

- **텔레메트리 3Hz가 병목이다.** 초음파 4~5개를 순서대로 재느라(각 최대 38ms
  타임아웃) 느려지는 것으로 보인다. 펌웨어에서 **IMU(yaw/gyro)만 따로 20Hz로**
  쏘게 하면 보정 품질이 확 올라간다. 지금 게인은 3Hz를 견디도록 보수적으로 잡혀 있다.
- **측면 초음파 4개가 전부 -1**(전방은 정상). 센서군 전원/배선 확인 필요.
- **`ultrasound/sample.ino`가 실제 플래시된 펌웨어와 다르다.** 실제 펌웨어에는
  MPU6050 코드(`imu_ready`/`yaw`/`gyro_z`/`yaw_toggle`)가 들어 있는데 저장소 버전에는
  없다. 실제 .ino를 커밋해야 한다.

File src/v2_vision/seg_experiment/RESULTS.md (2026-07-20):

# 세그멘테이션 실험 결과 (2026-07-10)

## 요약 (TL;DR)

**가설("번호판 마스크로 yaw 부호를 더 안정적으로 잴 수 있다")은 유망하다.**
20분짜리 로컬 맛보기 학습(100 epoch 중 13에서 계획 중단)만으로도 근거리
프레임에서 마스크가 번호판에 정확히 붙었고, 마스크 → 사다리꼴 꼭짓점 →
좌/우 변 길이 비교(키스톤)로 낸 yaw 부호가 검증 지점 3곳 중 2곳 정답.
틀린 1곳은 미성숙 모델의 마스크 노이즈가 원인 → **Kaggle 완주 학습으로
재검증할 가치 충분** (패키지 준비 완료, 아래 "다음 단계").

## 한 것

1. `prepare_seg_dataset.py` — ray_all(121장) → seg용 데이터셋
   (train 103 / valid 18, 박스 라벨 53개는 사각 폴리곤으로 변환)
2. `train_seg.py` — yolov8n-seg, MPS 로컬 학습. **13/100 epoch에서 계획 중단**
   (사용자 부재 일정 때문. best.pt는 매 epoch 저장되므로 유효)
3. `eval_seg.py` — 거리추정_정리.md에 육안 검증된 정답 프레임 4곳에서 평가

## 평가 결과 (epoch 13 모델, conf 0.15)

| 프레임 | 기대 | 검출 | 마스크 yaw 부호 |
|---|---|---|---|
| 영상1 1초 (우측 45°) | R(+) | 5개 | 변길이비 0.605 → **R(+) ✓** |
| 영상1 10초 (좌측 치우침) | L(-) | 5개 | 변길이비 1.495 → **L(-) ✓** |
| 영상3 20초 (우측 비스듬) | R(+) | 3개 | 변길이비 2.305 → **L(-) ✗** |
| 영상2 5초 (원거리 후면) | - | 1개 (tail만) | 번호판 미검출 |

- 이미지: `eval/*_masks.jpg` (전체 마스크), `eval/*_plate_mask.jpg` (번호판 확대)
- **영상1 1초 마스크는 육안으로도 번호판 윤곽에 깔끔하게 밀착** — 이 품질이면
  기존 Otsu 꼭짓점 검출(distance_video.py의 find_plate_quad)을 대체 가능한 수준
- **영상3 실패 원인**: 마스크가 번호판 밖(브래킷·차체)으로 새는 노이즈 →
  convex hull 꼭짓점이 왜곡. 13 epoch 미성숙 모델의 전형적 증상.
  참고: 이 프레임의 번호판은 다른 차("237허 5991")임 — 목표 차량 필터 미구현
  한계(README 기지사항)가 seg에서도 동일하게 존재
- 영상2 원거리 미검출도 미성숙 + 소형 객체 → 완주 학습 후 재평가 필요
- val 지표(epoch 13): mask mAP50 0.19 (탐지 v4의 0.9x 대비 낮음 — 13 epoch뿐이라
  당연. 완주 후 다시 볼 것)

## 배운 것 / 함정

- **minAreaRect로는 키스톤 측정 불가** (항상 완전한 직사각형을 반환해 좌/우 변이
  정의상 동일). convex hull → approxPolyDP 4각형 근사를 써야 함. eval_seg.py에 반영
- 세그 학습은 폴리곤 라벨만 허용 → 박스 53개 변환 필요했음 (prepare 스크립트가 처리)
- ray_all은 valid가 비어 있어 분할 필수 (여기선 85/15 프레임 랜덤, 시드 42)

## 다음 단계 (Kaggle 완주 학습 — 패키지 준비 완료)

1. kaggle.com → 기존 데이터셋에 `seg_experiment/ray_seg.bin` 추가 업로드
2. `seg_experiment/kaggle_seg.ipynb` 노트북 업로드 → T4, Internet On →
   Add Input에 ray_seg.bin 데이터셋 연결 → 전체 실행 (100 epoch, patience 25)
3. `/kaggle/working/runs/seg_full/weights/best.pt` 다운로드 →
   `seg_experiment/runs/seg_full_best.pt`로 저장
4. 재평가: `python3.10 seg_experiment/eval_seg.py seg_experiment/runs/seg_full_best.pt`
5. 그 결과가 좋으면: distance_video.py의 find_plate_quad(Otsu)를 마스크 기반으로
   교체하는 것 검토 + 후미등 "안쪽 변" 기준 각도 재도전

## 파일

```
seg_experiment/
├── prepare_seg_dataset.py  # ray_all → seg 데이터셋 (원본 안 건드림)
├── train_seg.py            # 로컬 MPS 학습 스크립트
├── eval_seg.py             # 정답 프레임 4곳 평가 (모델 경로 인자로 교체 가능)
├── kaggle_seg.ipynb        # Kaggle T4 완주 학습용 노트북
├── ray_seg.bin             # Kaggle 업로드용 데이터셋 (55MB)
├── dataset/                # 로컬 seg 데이터셋 (train 103 / valid 18)
├── runs/seg_v1/            # 이번 13-epoch 실험 결과 (weights/best.pt)
├── eval/                   # 평가 이미지 (마스크 시각화)
└── train_log.txt           # 학습 로그
```

※ 본 실험은 전부 이 폴더 안에 격리됨. 기존 파이프라인(scripts/, models/,
my_data/labeled/ray_all)은 변경 없음. my_data/labeled/ray_all.bin(탐지 v5용)은
이전 작업에서 생성된 별개 파일.

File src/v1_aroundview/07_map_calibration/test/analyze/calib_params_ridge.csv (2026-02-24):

cam | lambda_xy | lambda_theta | feature_def | target | wpar_bias | wper_bias | wtheta_bias | wpar_g | wper_g | wtheta_g | wpar_g2 | wper_g2 | wtheta_g2 | wpar_b | wper_b | wtheta_b | wpar_b2 | wper_b2 | wtheta_b2 | wpar_v | wper_v | wtheta_v | wpar_g*b | wper_g*b | wtheta_g*b | wpar_reproj | wper_reproj | wtheta_reproj
rear | 1.0 | 20.0 | X=[1,g,g^2,abs(b),abs(b)^2,v,g*abs(b),reproj], fit e_par/e_perp in ray frame + dtheta | rear->GT, left->(1-a)*GT+a*rear_phys (pos+theta) | 11.411634184909698 | -1.8264648254163274 | -0.08487145442480232 | 13.036956040029038 | -2.7696363884551074 | -0.19859339844466445 | -0.19490675567789872 | -1.0640202560967764 | -0.8920894244268675 | 4.496420937828837 | -1.5412681329857396 | 1.440673574535577 | -0.044484666874107355 | 0.02275824177861486 | -0.018542139845957806 | -0.12237879592984628 | 0.14314837081863988 | -0.0372567551727219 | -0.9315966755096304 | -0.11749545938440137 | -0.0906682088386136 | 4.413657758841521 | -1.23342907837325 | 0.2366533369346807
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

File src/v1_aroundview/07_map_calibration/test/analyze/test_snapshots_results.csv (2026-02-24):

pair_key | cam | file | seq | gt_x | gt_y | gt_ang | status | pred_x | pred_y | pred_ang | pos_err_cm | ang_err_deg
100_360_45_1 | left | left_x100_y360_+45_1.jpg | 1 | 100 | 360 | 45 | ok | 98.62239480749189 | 360.71384988530485 | 43.518233858609165 | 1.5515726619063215 | 1.4817661413908354
100_360_45_1 | fused |  | 1 | 100 | 360 | 45 | ok | 98.62239480749189 | 360.71384988530485 | 43.518233858609165 | 1.5515726619063215 | 1.4817661413908354
100_360_45_2 | left | left_x100_y360_+45_2.jpg | 2 | 100 | 360 | 45 | ok | 98.62239480749189 | 360.71384988530485 | 43.518233858609165 | 1.5515726619063215 | 1.4817661413908354
100_360_45_2 | fused |  | 2 | 100 | 360 | 45 | ok | 98.62239480749189 | 360.71384988530485 | 43.518233858609165 | 1.5515726619063215 | 1.4817661413908354
100_360_45_3 | left | left_x100_y360_+45_3.jpg | 3 | 100 | 360 | 45 | ok | 99.62590703355454 | 358.2995336836767 | 46.094876760867805 | 1.7411293003375856 | 1.0948767608678054
100_360_45_3 | fused |  | 3 | 100 | 360 | 45 | ok | 99.62590703355454 | 358.2995336836767 | 46.094876760867805 | 1.7411293003375856 | 1.0948767608678054
100_360_-45_1 | left | left_x100_y360_-45_1.jpg | 1 | 100 | 360 | -45 | no_marker
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

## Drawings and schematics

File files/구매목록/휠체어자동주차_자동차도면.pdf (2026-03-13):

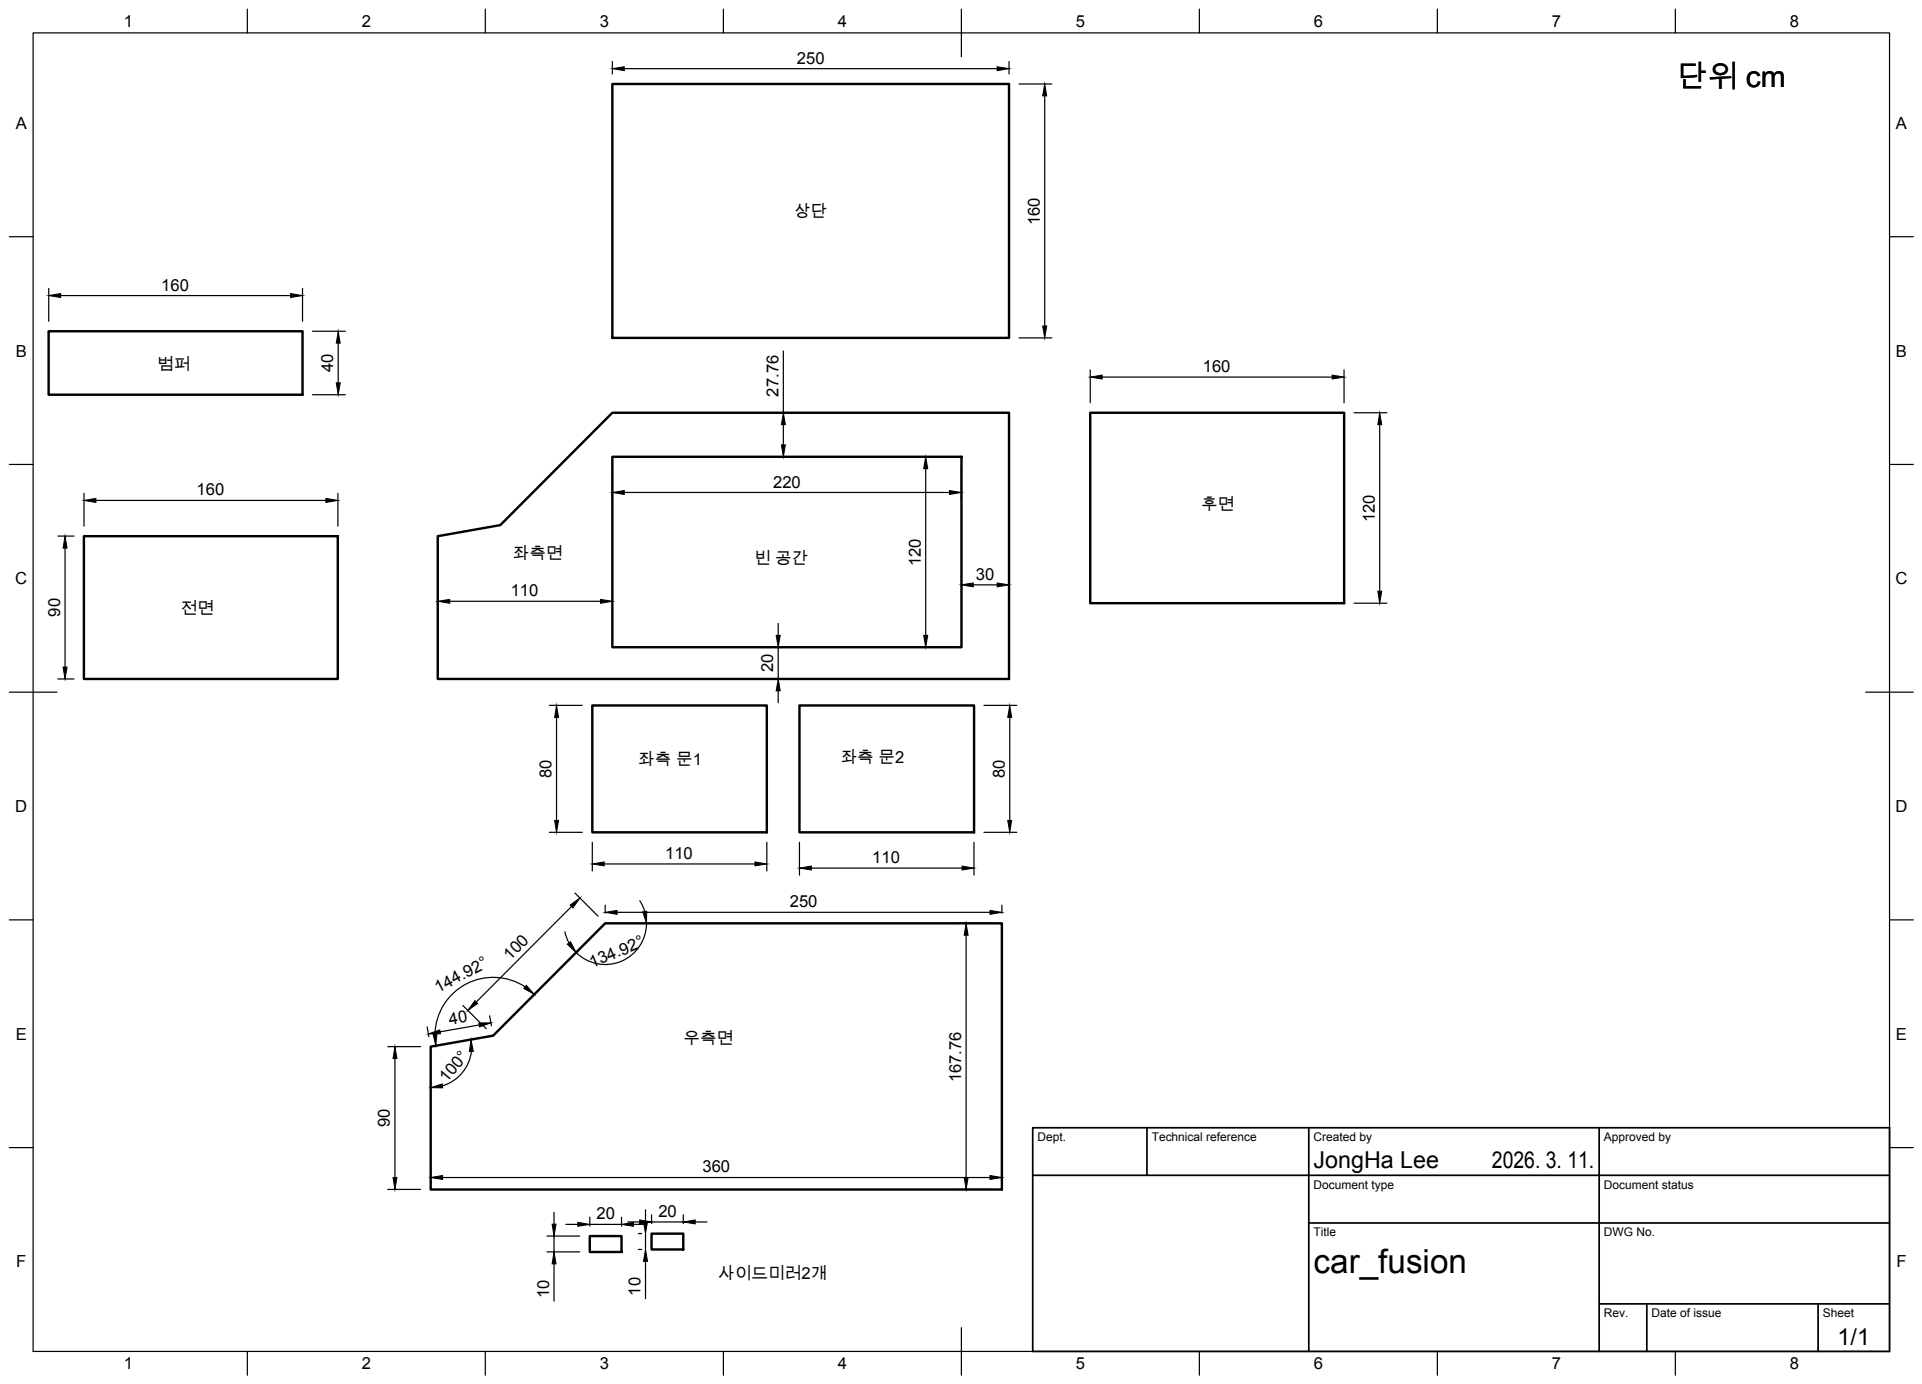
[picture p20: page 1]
Title; DWG No.; Rev.; Date of issue; Sheet; 좌측면

Dept. | Technical reference | Created by JongHa Lee 2026. 3. 11. | Approved by

Document type | Document status

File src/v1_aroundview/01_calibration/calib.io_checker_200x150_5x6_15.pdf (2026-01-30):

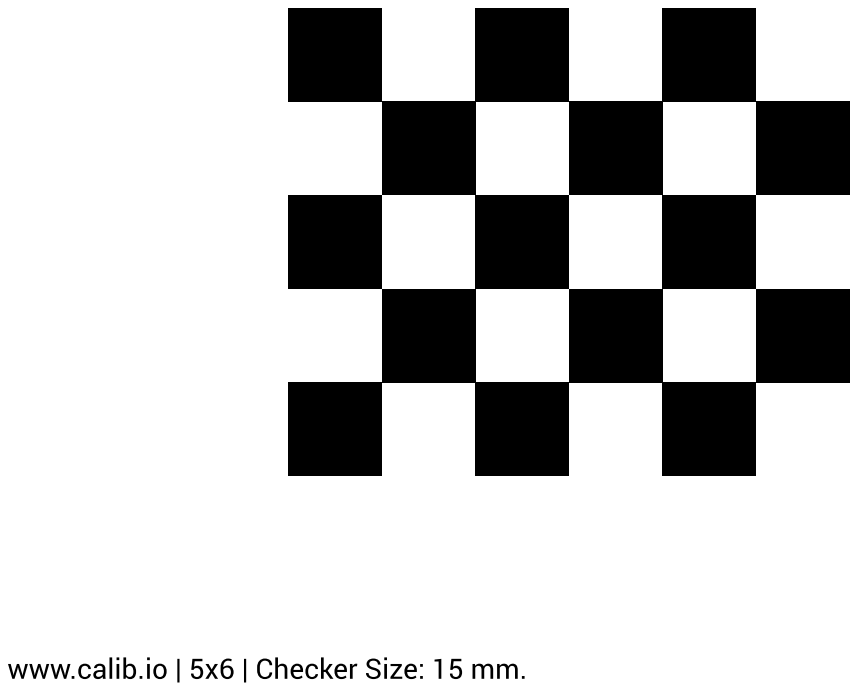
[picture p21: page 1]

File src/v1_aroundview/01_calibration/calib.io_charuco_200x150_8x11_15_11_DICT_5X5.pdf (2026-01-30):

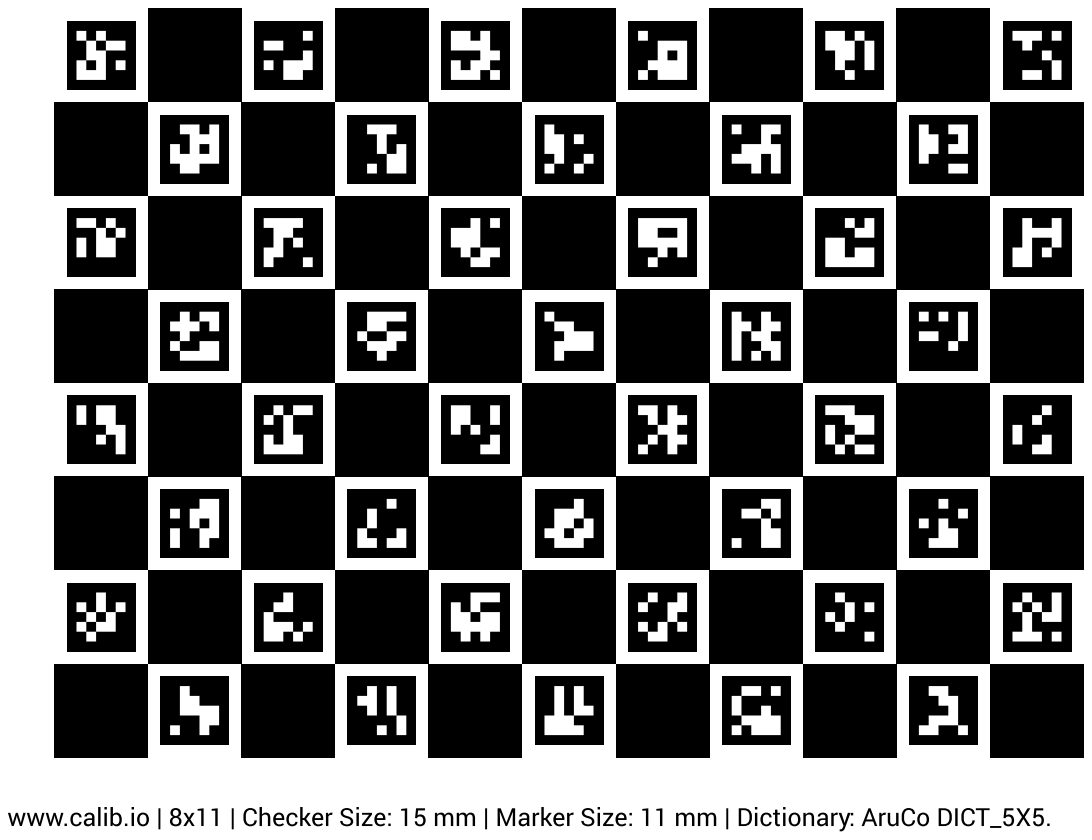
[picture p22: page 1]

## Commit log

2026-01-27 connect구성
2026-01-29 폴더정리
2026-02-03 command case update
2026-02-03 test delete
    [clamp.3mf]
2026-02-24 mapcalibration add
    [calib_params_ridge.csv, test_snapshots_results.csv, tocsv.csv, tocsv_calib.csv]
2026-02-25 Refactor localization calculations with weighted averages
    Refactor localization logic to use weighted averages for center position and heading, and apply calibration offsets.
2026-02-27 발표자료
